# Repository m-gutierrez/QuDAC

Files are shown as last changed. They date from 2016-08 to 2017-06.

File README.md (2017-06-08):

# QuDAC

***TODO
+	Update performance measurements
+	include pin-out maps
+	link to ion trap theory, for voltage requirement definitions. 
+	include BOM
+	include assembly photos

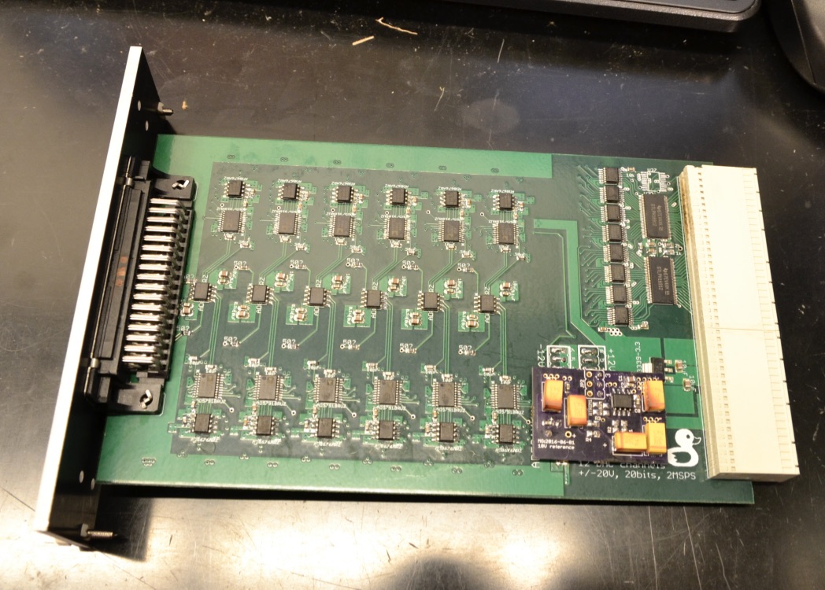
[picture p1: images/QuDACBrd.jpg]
QuDAC


This is a 12-channel 20-bit, +/-10V (+/-20V optional) 2MSPS DAC board designed for the Quanta rack system (QuACK). The card was designed to meet the system requirements described bellow while also being simple to populate and interface with the Quanta ion trap system vacuum chamber. Since we assemble these by-hand, we desired as few components as possible while still meeting the requirements of precision experiments with trapped ions. All components should be standard and easy to source, and if possible relatively cheap. A huge exception to the cheap criterion was the use of the ad5791 DAC chip, however there is a a slightly cheaper 18-bit ad5781 which is a drop-in replacement, and a significantly cheaper 16-bit version which requires modification for the different package size.

We've tested the cards at +/-10V, and have achieved reliable update rates at 2MSPS (above the 1.33MSPS datasheet spec for ad5791). Output slew's of ~50V/us have been measured on voltage swings >1V. Noise output is DAC-code dependent, currently limited by the reference-noise (~100nV/sqrt(Hz)). Which We've improved by using an adapter reference board with heavy filtering, 3-pole 1.5Hz cut-off RC filter with capacitors in a bootstrap configuration to minimize offset errors, which reduces the white-noise level to that dominated by the DAC and output op-amp of ~10-20nV/sqrt(Hz) white noise beyond 1kHz.

## Layout 

The board contains 6-layers. This was mostly due to a panel order with other designs requiring 6 layers. The board could easily be re-drawn with 4 layers.
The current layout is 

+	layer 1 - analog signals (top)
+	layer 2 - ground plane
+	layer 3 - analog signals
+	layer 4 - power planes
+	layer 5 - ground plane
+	layer 6 - digital signals (bot)

## component choice

The components where chosen to meet the system requirements, here is a list of the key QuDAC components with a list of the relevant performance spec's.

+	AD5791: DAC, 20-bit, +/-15V supply range, NSD <10nV/sqrt(Hz), 1-2MSPS update rate
+	AD8676: op-amp, +/-15V supply range, NSD <10nV/sqrt(Hz), 10MHz GBP
+	AD8620: op-amp, +/-12V supply range, NSD <10nV/sqrt(Hz), 50MHz GBP, <1us settling to 20-bit accuracy
+	See card-buffer for description of backplane interface.

## Application aim 

Trapped ion quantum computing (TIQC) requires dozens of independently controllable voltage sources with low noise (<100nV/sqrt(Hz)), wide-output range (+/-10V) and fast update rates (>1MSPS). These sources should be extend-able while maintaining synchronized updates, and allow for asynchronous clocking. 

### Output range

In the trap for our particular experiment, Sandia's high optical access trap (HOA v2), there are 96 independent control electrodes. With a trapping height ~68micron, an electrode pitch of ~70micron and control electrodes between the RF electrodes the HOA requires voltages of ~1-4V for trapping potentials producing secular frequencies $\omega_{sec} \approx 2\pi 1MHz$. And allows for +/-20V without damage to the on-chip RF-shunting capacitors. 

### Precision

### Noise level

For room temperature traps typical electric field noise at the ion, due to yet-unknown surface effects, is around ($S_{\nu} \approx 10 \mu V /m\sqrt{Hz}$), which corresponds to an electrode-voltage noise of (~100nV/sqrt(Hz)). Electric field noise in ion traps is a major concern for high fidelity operations, as current two-qubit gate mechanisms use the ions motional state and are first order sensitive to changes in the motional state during the gate operation. In order for gate fidelities to reach error correcting thresholds of ~1e-4 control-voltage noise must be kept well bellow this value. 

### Update rates

Control potentials used in TIQC is typically a compromise between many different concerns. One such concern is that the electric field noise spectrum typical goes as ~1/f such that increasing the secular frequencies is one way to reduce the error due to motional heating of the ion. Another is trap stability and overall trapping depth, since the axial-potential can easily over-take the radial psuedo-potential and reduce the trapping depth to zero. For the trapping dimensions typical used (heights of 50-150micron) useful compromises tend to be between 1-2MHz axial secular frequencies. 

This sets the time scale how changes to control voltages will affect the ions motion, i.e. the time scale for changes to be adiabatic or diabatic. We would like voltage updates to be on the order of or faster than the characteristic ion motion, so update rates exceeding 1MSPS and slew rates >1V/MHz are necessary to meet this constraint. 

### synchronized updates and clocking
The density of the DAC's per card and the clocking rate. where chosen to meet more general back-plane specifications, which takes into account additional devices of interest, clocking speeds, types of isolation achievable over various clock speeds and bus-size. In the end, a 36-bit backplane bus allows for 12-DAC's with independent sync,clock and data lines. In addition to these 36-bits there are an additional 8-bits which by-pass the card select buffers on the backplane interface, which we connect the DAC update pin (LDAC) to allowing multiple cards to be updated simultaneously. 

# Adapters 

There are 3 adapter cards used in our setup. Which assist in converting the card channels into the experiments two DB-50 connectors. 

## Combine2Cards
The first `Combine2Cards' allows us to combine two of the QuDAC cards into a single 24 channel output. The card can be placed directly on the cards within the rack, designed for accommodate the 7HP spacing of the QuACK system. The pin-out is made such that each control voltage is routed as a twisted pair with a ground wire using standard db50 cables. 

## 24CH-2x24CH
The second card, '24CH-2x24CH', copies one 24 channel output into 2 identical pin-out 24-channel outputs. Allowing 48 DAC's to control all 96 trap control voltages. The card also has a 3rd copy for probing voltage outputs.

## filterboard
The final card, 'filterboard', takes two 24-channel inputs and routes them into a single db50-connector. The board also contains 48 7-pole (or 3-pole) coilcraft.com LC filters. In our setup, these are 7-pole 300kHz LC-filters, providing 80db suppression at 1-2MHz. This board is intended to plug directly into the vacuum chamber experiment flange, which routes 100 control signals into the trap-chip through two DB-50 connectors. One of thees boards should also be configured with the resonator-line populated. On our setup, this line consists of a hand-wound ~500nH inductor, connecting to ~20pF trap capacitance producing a ~50MHz resonant frequency, and ~300pF of matching capacitance. The RF tap, consists of a high-voltage 0.2pF capacitor and a 100pF capacitor for a ~1/500 sampling voltage gain. 

# System performance

## range, offset and non-linearity

## noise spectral density

## update rate, slew rate, tone-purity

## synchronous update, clock noise

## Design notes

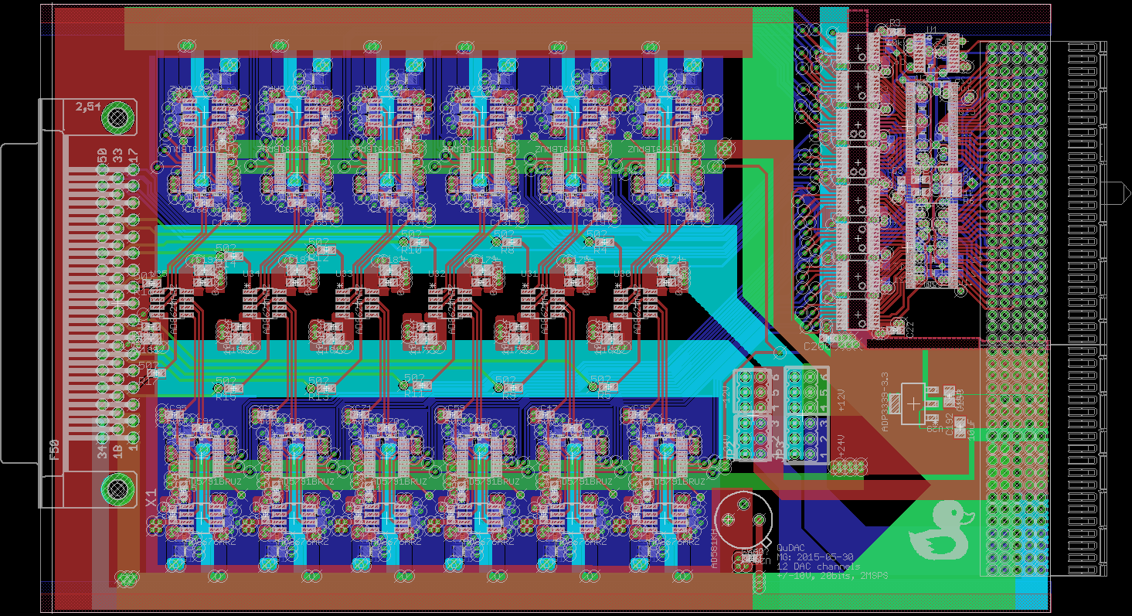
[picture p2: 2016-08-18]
images/QuDACBrd.png

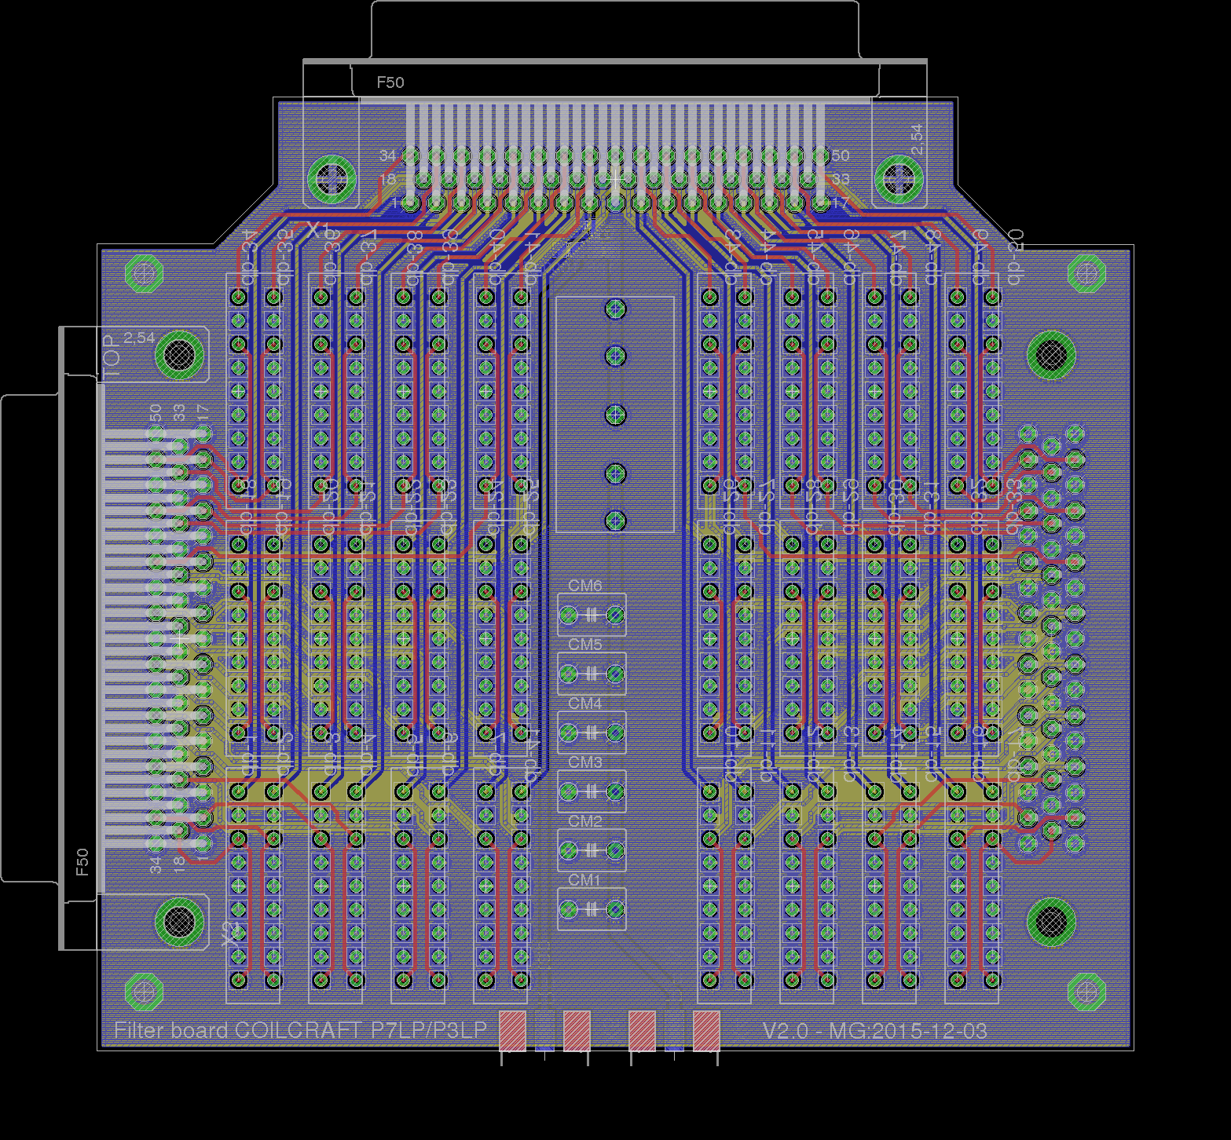
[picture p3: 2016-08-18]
images/filterboard.png

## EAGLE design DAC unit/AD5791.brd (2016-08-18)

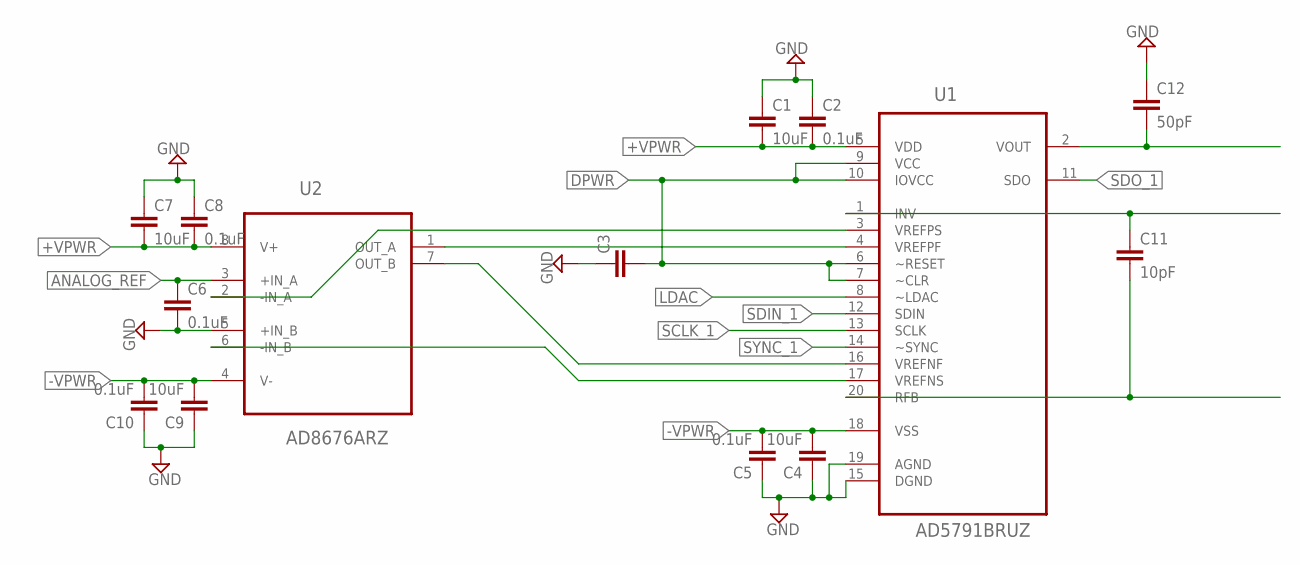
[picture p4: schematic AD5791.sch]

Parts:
C1, C4, C7, C9: 10uF; C0805
C2, C5, C6, C8, C10: 0.1uF; C0603
C3: CC0603; C0603
C11: 10pF; C0603
C12: 50pF; C0603
U1: AD5791BRUZ; SOP65P640X120-20N
U2: AD8676ARZ; SOIC127P600X175-8N

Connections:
+VPWR: C1.2, C2.2, C7.2, C8.2, U1.5 (VDD), U2.8 (V+)
-VPWR: C4.2, C5.2, C9.2, C10.2, U1.18 (VSS), U2.4 (V-)
ANALOG_REF: C6.1, U2.3 (+IN_A)
DPWR: C3.2, U1.6 (~RESET), U1.7 (~CLR), U1.9 (VCC), U1.10 (IOVCC)
GND: C1.1, C2.1, C3.1, C4.1, C5.1, C6.2, C7.1, C8.1, C9.1, C10.1, C12.1, U1.15 (DGND), U1.19 (AGND), U2.5 (+IN_B)
LDAC: U1.8 (~LDAC)
unnamed: U1.4 (VREFPF), U2.1 (OUT_A)
unnamed: U1.16 (VREFNF), U2.7 (OUT_B)
unnamed: U1.3 (VREFPS), U2.2 (-IN_A)
unnamed: U1.17 (VREFNS), U2.6 (-IN_B)
unnamed: C12.2, U1.2 (VOUT)
unnamed: C11.1, U1.1 (INV)
unnamed: C11.2, U1.20 (RFB)
SCLK_1: U1.13 (SCLK)
SDIN_1: U1.12 (SDIN)
SDO_1: U1.11 (SDO)
SYNC_1: U1.14 (~SYNC)

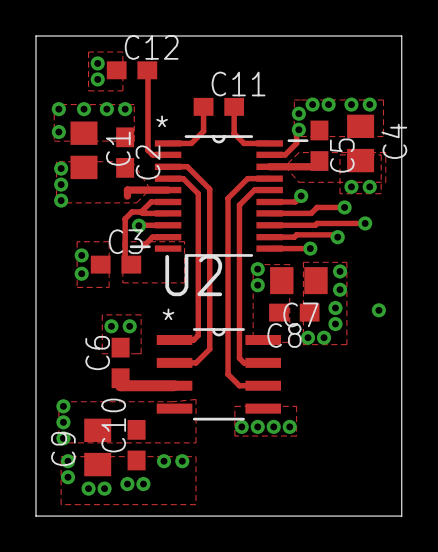
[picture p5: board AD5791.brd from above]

Board: 4 copper layers, 20.3 x 26.7 mm, 14 parts (0 on the bottom side), 12 nets.

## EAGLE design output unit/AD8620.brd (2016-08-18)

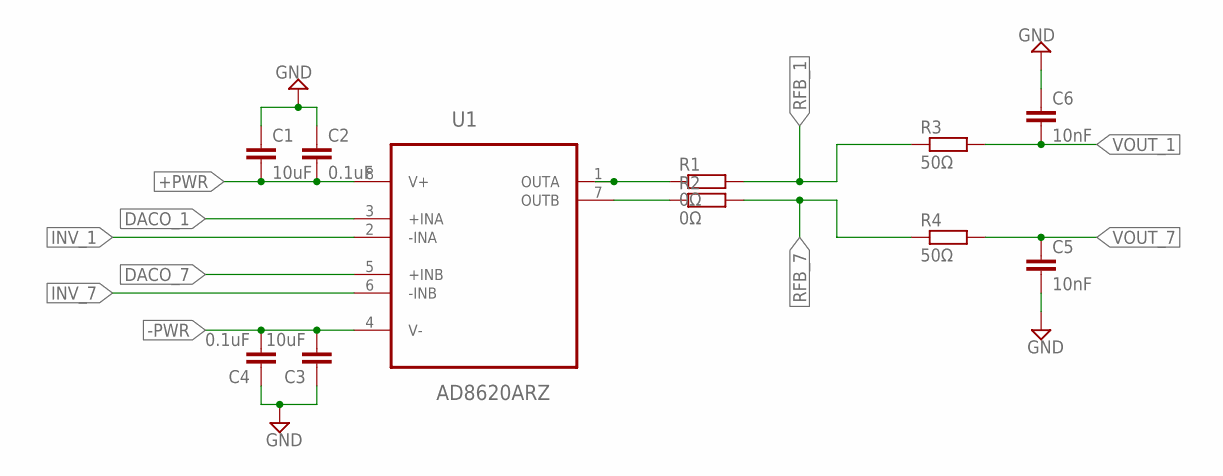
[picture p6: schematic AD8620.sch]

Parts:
C1, C3: 10uF; C0805
C2, C4: 0.1uF; C0603
C5, C6: 10nF; C0603
R1, R2: 0Ω; R0603
R3, R4: 50Ω; R0603
U1: AD8620ARZ; SOIC127P600X175-8N

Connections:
+PWR: C1.2, C2.2, U1.8 (V+)
-PWR: C3.2, C4.2, U1.4 (V-)
DACO_1: U1.3 (+INA)
DACO_7: U1.5 (+INB)
GND: C1.1, C2.1, C3.1, C4.1, C5.2, C6.1
INV_1: U1.2 (-INA)
INV_7: U1.6 (-INB)
unnamed: R1.1, U1.1 (OUTA)
unnamed: R2.1, U1.7 (OUTB)
RFB_1: R1.2, R3.1
RFB_7: R2.2, R4.1
VOUT_1: C6.2, R3.2
VOUT_7: C5.1, R4.2

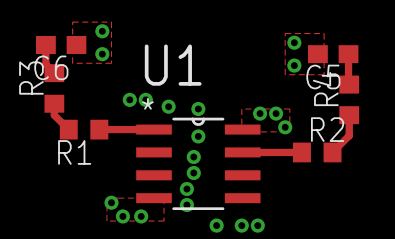
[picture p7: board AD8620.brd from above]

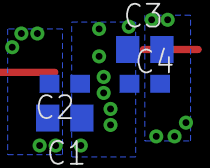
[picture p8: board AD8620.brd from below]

Board: 6 copper layers, 11 parts (4 on the bottom side), 9 nets.

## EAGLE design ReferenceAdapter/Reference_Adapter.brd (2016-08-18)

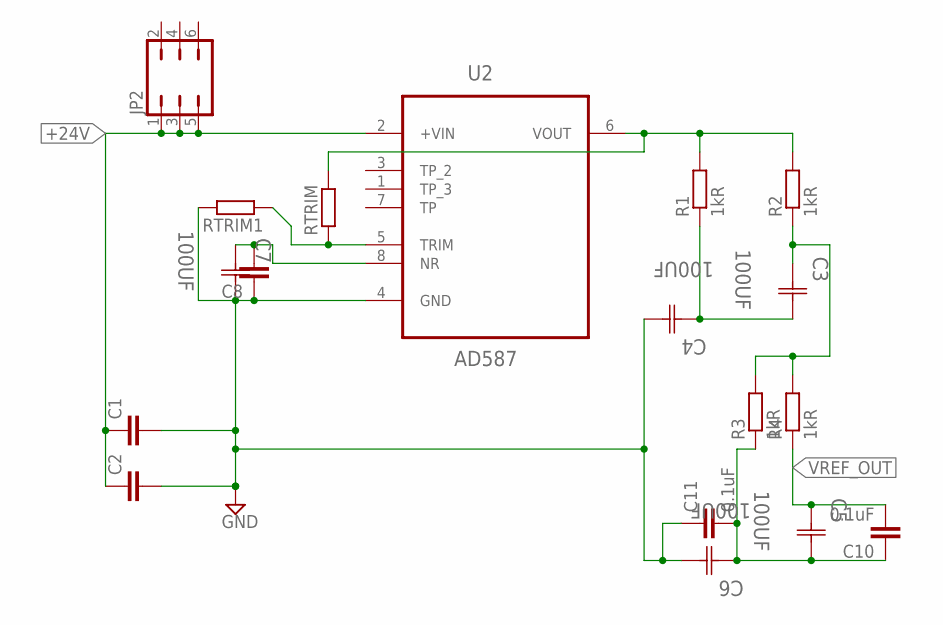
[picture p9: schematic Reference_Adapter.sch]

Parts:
C1, C8: C; C0805
C2: CC0603; C0603
C3, C4, C5, C6, C7: 100UF; CAPCP7343X430N
C10, C11: 0.1uF; C0603
JP2: JP3Q
R1, R2, R3, R4: 1kR; R0805
RTRIM, RTRIM1: R; R0805
U2: AD587; SOIC127P600X175-8N

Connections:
+24V: C1.1, C2.1, JP2.1, JP2.3, JP2.5, U2.2 (+VIN)
GND: C1.2, C2.2, C4.2, C6.2, C7.2, C8.1, C11.1, RTRIM1.2, U2.4 (GND)
unnamed: C3.2, C4.1, R1.1
unnamed: RTRIM.1, RTRIM1.1, U2.5 (TRIM)
unnamed: R1.2, R2.2, RTRIM.2, U2.6 (VOUT)
unnamed: C7.1, C8.2, U2.8 (NR)
unnamed: C3.1, R2.1, R3.2, R4.2
unnamed: C5.2, C6.1, C10.1, C11.2, R3.1
VREF_OUT: C5.1, C10.2, R4.1

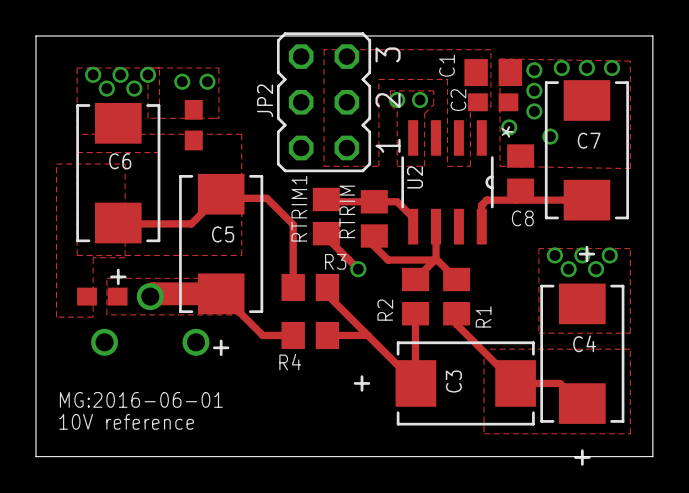
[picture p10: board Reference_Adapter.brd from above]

Board: 2 copper layers, 34.3 x 23.4 mm, 18 parts (0 on the bottom side), 9 nets.

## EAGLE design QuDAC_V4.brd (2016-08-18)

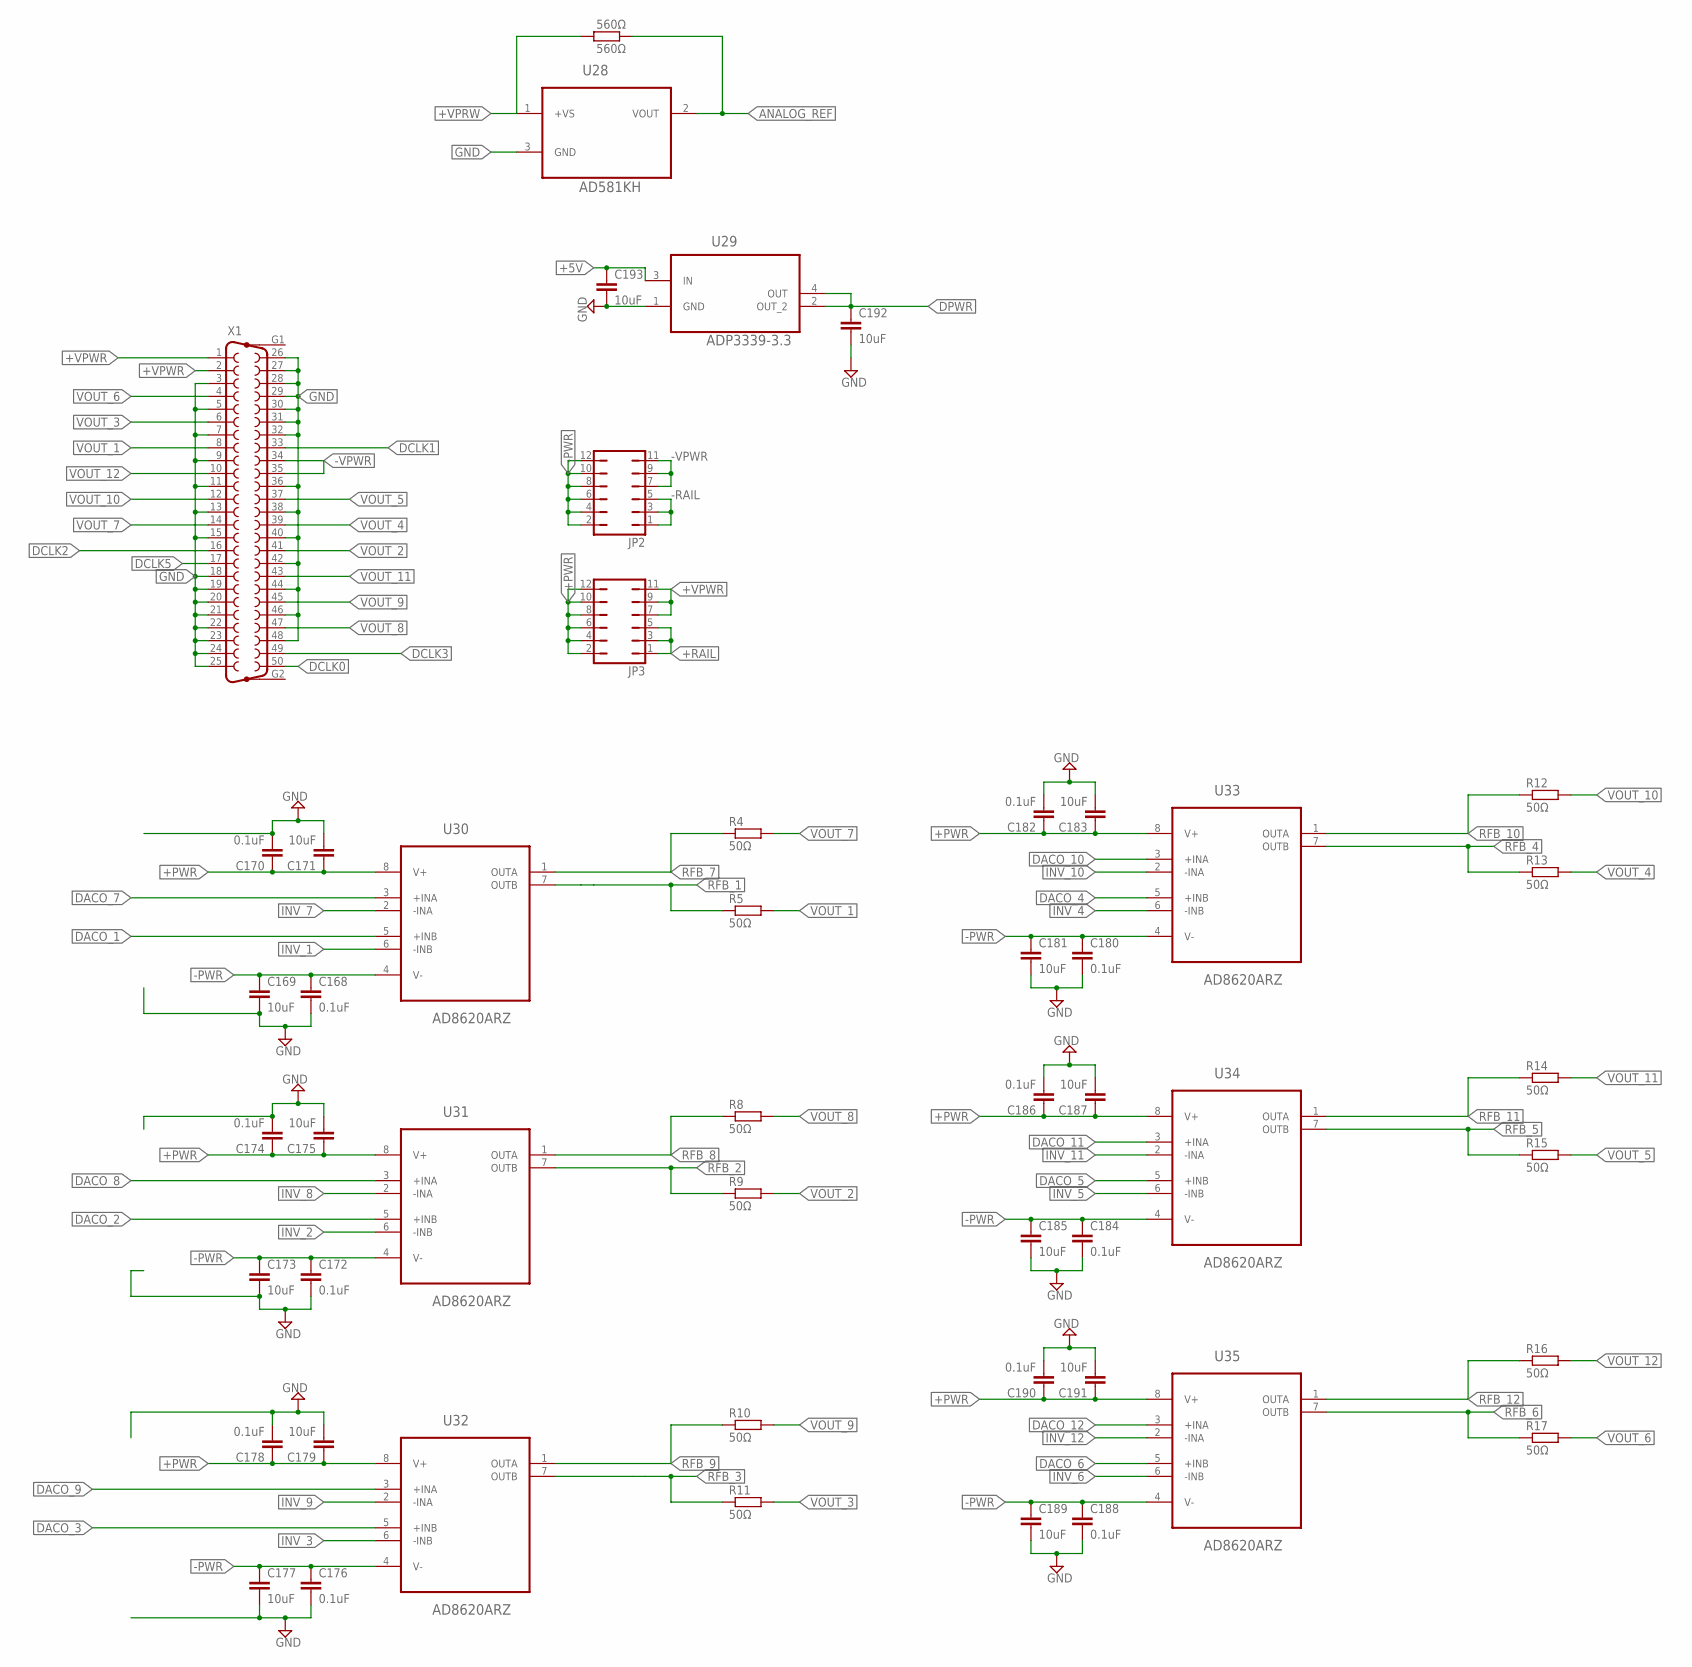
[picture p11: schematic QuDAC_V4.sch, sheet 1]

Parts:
560Ω: 560Ω; R0603
C168, C170, C172, C174, C176, C178, C180, C182, C184, C186, C188, C190: 0.1uF; C0603
C169, C171, C173, C175, C177, C179, C181, C183, C185, C187, C189, C191, C192, C193: 10uF; C0805
JP2, JP3: JP6Q
R4, R5, R8, R9, R10, R11, R12, R13, R14, R15, R16, R17: 50Ω; R0603
U28: AD581KH; TO254P939X470-3P
U29: ADP3339-3.3; SOT230P700X180-4N
U30, U31, U32, U33, U34, U35: AD8620ARZ; SOIC127P600X175-8N
X1: F50HP

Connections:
+5V: C193.1, U29.3 (IN); also elsewhere on the board
+PWR: C170.1, C171.1, C174.1, C175.1, C178.1, C179.1, C182.1, C183.1, C186.1, C187.1, C190.1, C191.1, JP3.2, JP3.4, JP3.6, JP3.8, JP3.10, JP3.12, U30.8 (V+), U31.8 (V+), U32.8 (V+), U33.8 (V+), U34.8 (V+), U35.8 (V+)
+RAIL: JP3.1, JP3.3, JP3.5; also elsewhere on the board
+VPRW: 560Ω.2, U28.1 (+VS)
+VPWR: JP3.7, JP3.9, JP3.11, X1.1, X1.2; also elsewhere on the board
-PWR: C168.1, C169.1, C172.1, C173.1, C176.1, C177.1, C180.1, C181.1, C184.1, C185.1, C188.1, C189.1, JP2.2, JP2.4, JP2.6, JP2.8, JP2.10, JP2.12, U30.4 (V-), U31.4 (V-), U32.4 (V-), U33.4 (V-), U34.4 (V-), U35.4 (V-)
-RAIL: JP2.1, JP2.3, JP2.5; also elsewhere on the board
-VPWR: JP2.7, JP2.9, JP2.11, X1.34, X1.35; also elsewhere on the board
ANALOG_REF: 560Ω.1, U28.2 (VOUT); also elsewhere on the board
DACO_1: U30.5 (+INB); also elsewhere on the board
DACO_2: U31.5 (+INB); also elsewhere on the board
DACO_3: U32.5 (+INB); also elsewhere on the board
DACO_4: U33.5 (+INB); also elsewhere on the board
DACO_5: U34.5 (+INB); also elsewhere on the board
DACO_6: U35.5 (+INB); also elsewhere on the board
DACO_7: U30.3 (+INA); also elsewhere on the board
DACO_8: U31.3 (+INA); also elsewhere on the board
DACO_9: U32.3 (+INA); also elsewhere on the board
DACO_10: U33.3 (+INA); also elsewhere on the board
DACO_11: U34.3 (+INA); also elsewhere on the board
DACO_12: U35.3 (+INA); also elsewhere on the board
DCLK0: X1.50; also elsewhere on the board
DCLK1: X1.33; also elsewhere on the board
DCLK2: X1.16; also elsewhere on the board
DCLK3: X1.49; also elsewhere on the board
DCLK5: X1.17; also elsewhere on the board
DPWR: C192.1, U29.2 (OUT_2), U29.4 (OUT); also elsewhere on the board
GND: C168.2, C169.2, C170.2, C171.2, C172.2, C173.2, C174.2, C175.2, C176.2, C177.2, C178.2, C179.2, C180.2, C181.2, C182.2, C183.2, C184.2, C185.2, C186.2, C187.2, C188.2, C189.2, C190.2, C191.2, C192.2, C193.2, U28.3 (GND), U29.1 (GND), X1.3, X1.5, X1.7, X1.9, X1.11, X1.13, X1.15, X1.18, X1.19, X1.20, X1.21, X1.22, X1.23, X1.24, X1.25, X1.26, X1.27, X1.28, X1.29, X1.30, X1.31, X1.32, X1.36, X1.38, X1.40, X1.42, X1.44, X1.46, X1.48; also elsewhere on the board
INV_1: U30.6 (-INB); also elsewhere on the board
INV_2: U31.6 (-INB); also elsewhere on the board
INV_3: U32.6 (-INB); also elsewhere on the board
INV_4: U33.6 (-INB); also elsewhere on the board
INV_5: U34.6 (-INB); also elsewhere on the board
INV_6: U35.6 (-INB); also elsewhere on the board
INV_7: U30.2 (-INA); also elsewhere on the board
INV_8: U31.2 (-INA); also elsewhere on the board
INV_9: U32.2 (-INA); also elsewhere on the board
INV_10: U33.2 (-INA); also elsewhere on the board
INV_11: U34.2 (-INA); also elsewhere on the board
INV_12: U35.2 (-INA); also elsewhere on the board
RFB_1: R5.1, U30.7 (OUTB); also elsewhere on the board
RFB_2: R9.1, U31.7 (OUTB); also elsewhere on the board
RFB_3: R11.1, U32.7 (OUTB); also elsewhere on the board
RFB_4: R13.1, U33.7 (OUTB); also elsewhere on the board
RFB_5: R15.1, U34.7 (OUTB); also elsewhere on the board
RFB_6: R17.1, U35.7 (OUTB); also elsewhere on the board
RFB_7: R4.1, U30.1 (OUTA); also elsewhere on the board
RFB_8: R8.1, U31.1 (OUTA); also elsewhere on the board
RFB_9: R10.1, U32.1 (OUTA); also elsewhere on the board
RFB_10: R12.1, U33.1 (OUTA); also elsewhere on the board
RFB_11: R14.1, U34.1 (OUTA); also elsewhere on the board
RFB_12: R16.1, U35.1 (OUTA); also elsewhere on the board
VOUT_1: R5.2, X1.8
VOUT_2: R9.2, X1.41
VOUT_3: R11.2, X1.6
VOUT_4: R13.2, X1.39
VOUT_5: R15.2, X1.37
VOUT_6: R17.2, X1.4
VOUT_7: R4.2, X1.14
VOUT_8: R8.2, X1.47
VOUT_9: R10.2, X1.45
VOUT_10: R12.2, X1.12
VOUT_11: R14.2, X1.43
VOUT_12: R16.2, X1.10

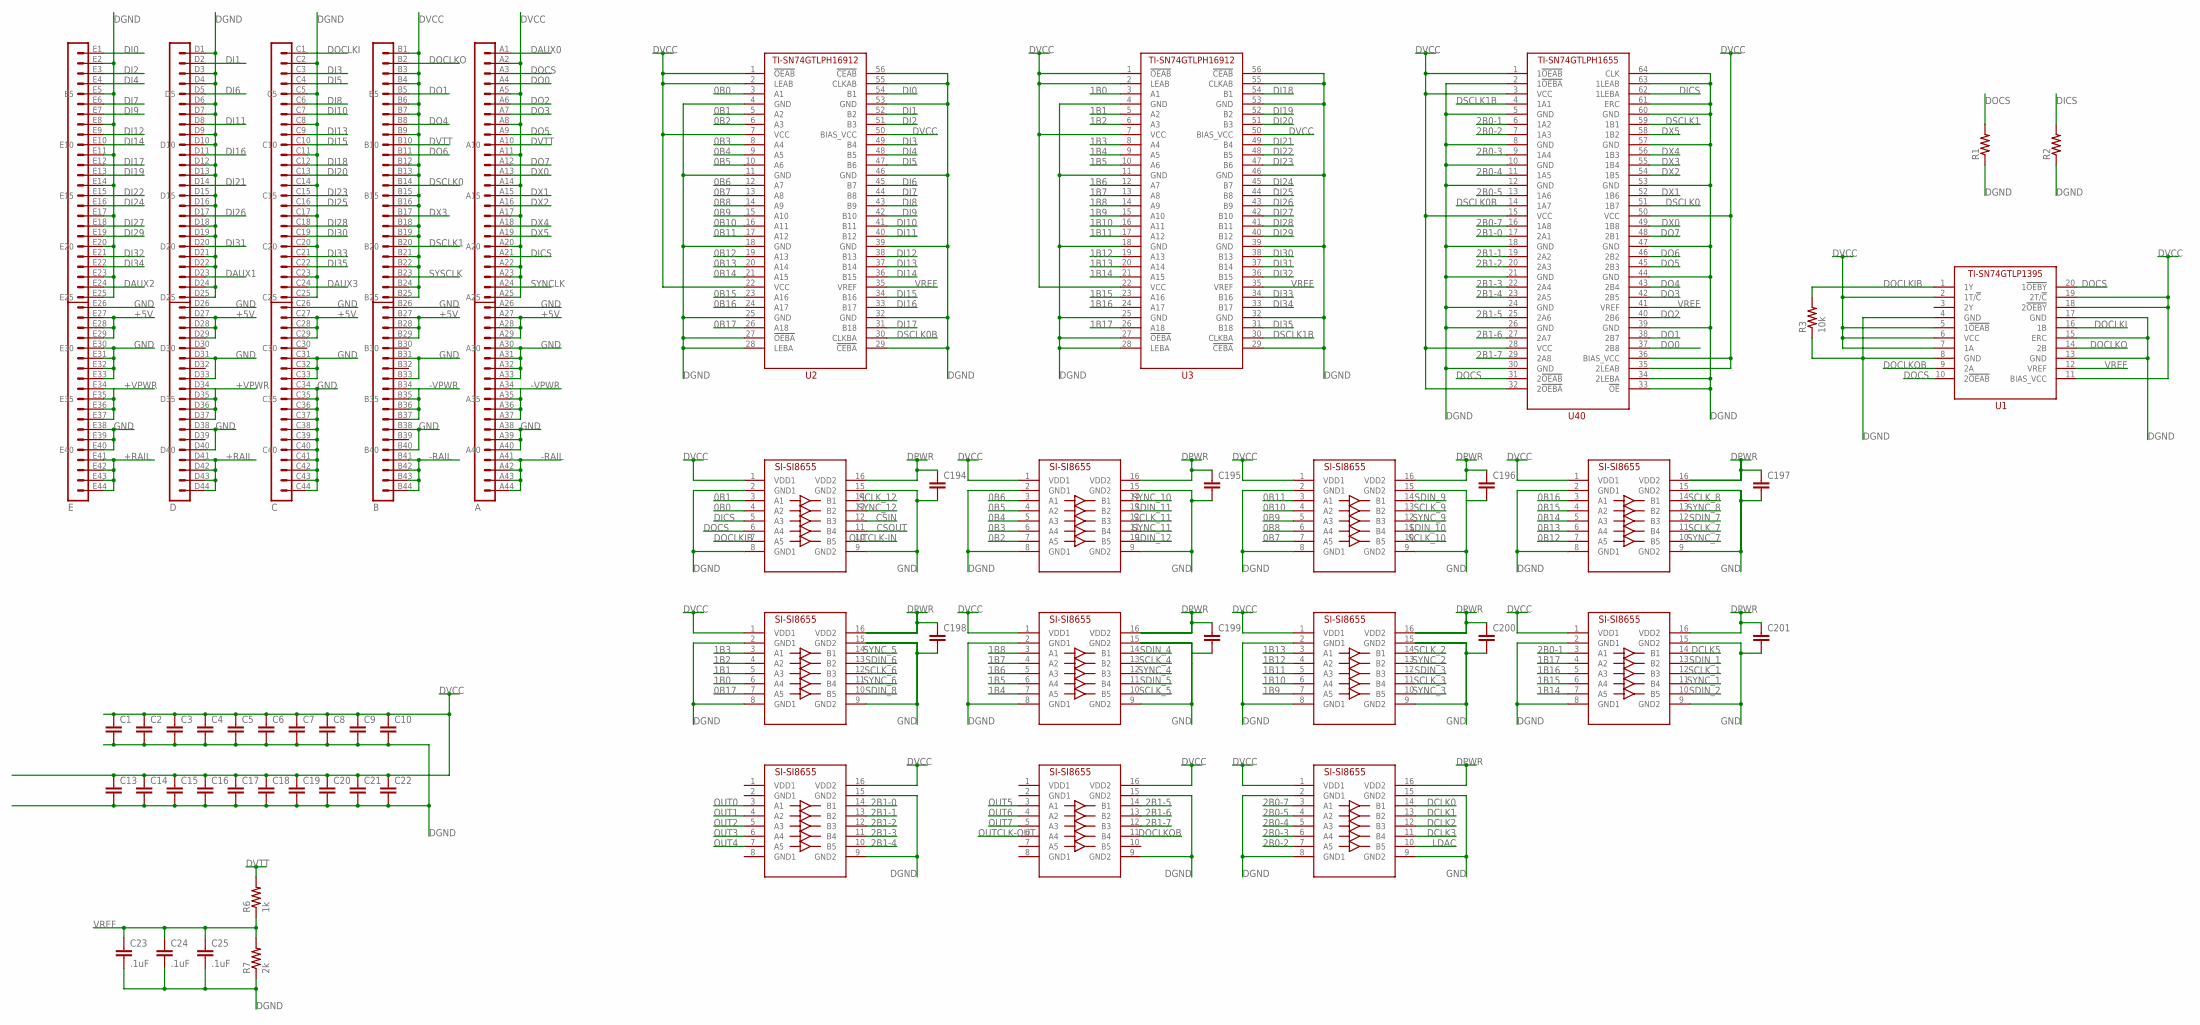
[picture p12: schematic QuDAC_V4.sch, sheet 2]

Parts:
C1, C2, C3, C4, C5, C6, C7, C8, C9, C10, C13, C14, C15, C16, C17, C18, C19, C20, C21, C22, C194, C195, C196, C197, C198, C199, C200, C201: CC0603; C0603
C23, C24, C25: .1uF; C0603
ISO1, ISO2, ISO3, ISO4, ISO5, ISO6, ISO7, ISO8, ISO9, ISO10, ISO11: SI-SI8655; QSOP-16
J1: EUROCARD-CPCI-220EUROCARD-B19+AB25-NOFRONTDIM; EUROCARD-CPCI-B19+1B25-NOFRONTDIM
R1, R2: R-US_R0603; R0603
R3: 10k; R0603
R6: 1k; R0805
R7: 2k; R0805
U1: TI-SN74GTLP1395; TSSOP-20
U2, U3: TI-SN74GTLPH16912; TSSOP-56
U40: TI-SN74GTLPH1655; TSSOP-64

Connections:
0B0: ISO1.4 (A2), U2.3 (A1)
0B1: ISO1.3 (A1), U2.5 (A2)
0B2: ISO2.7 (A5), U2.6 (A3)
0B3: ISO2.6 (A4), U2.8 (A4)
0B4: ISO2.5 (A3), U2.9 (A5)
0B5: ISO2.4 (A2), U2.10 (A6)
0B6: ISO2.3 (A1), U2.12 (A7)
0B7: ISO3.7 (A5), U2.13 (A8)
0B8: ISO3.6 (A4), U2.14 (A9)
0B9: ISO3.5 (A3), U2.15 (A10)
0B10: ISO3.4 (A2), U2.16 (A11)
0B11: ISO3.3 (A1), U2.17 (A12)
0B12: ISO4.7 (A5), U2.19 (A13)
0B13: ISO4.6 (A4), U2.20 (A14)
0B14: ISO4.5 (A3), U2.21 (A15)
0B15: ISO4.4 (A2), U2.23 (A16)
0B16: ISO4.3 (A1), U2.24 (A17)
0B17: ISO5.7 (A5), U2.26 (A18)
1B0: ISO5.6 (A4), U3.3 (A1)
1B1: ISO5.5 (A3), U3.5 (A2)
1B2: ISO5.4 (A2), U3.6 (A3)
1B3: ISO5.3 (A1), U3.8 (A4)
1B4: ISO6.7 (A5), U3.9 (A5)
1B5: ISO6.6 (A4), U3.10 (A6)
1B6: ISO6.5 (A3), U3.12 (A7)
1B7: ISO6.4 (A2), U3.13 (A8)
1B8: ISO6.3 (A1), U3.14 (A9)
1B9: ISO7.7 (A5), U3.15 (A10)
1B10: ISO7.6 (A4), U3.16 (A11)
1B11: ISO7.5 (A3), U3.17 (A12)
1B12: ISO7.4 (A2), U3.19 (A13)
1B13: ISO7.3 (A1), U3.20 (A14)
1B14: ISO8.7 (A5), U3.21 (A15)
1B15: ISO8.6 (A4), U3.23 (A16)
1B16: ISO8.5 (A3), U3.24 (A17)
1B17: ISO8.4 (A2), U3.26 (A18)
2B0-1: ISO8.3 (A1), U40.6 (1A2)
2B0-2: ISO11.7 (A5), U40.7 (1A3)
2B0-3: ISO11.6 (A4), U40.9 (1A4)
2B0-4: ISO11.5 (A3), U40.11 (1A5)
2B0-5: ISO11.4 (A2), U40.13 (1A6)
2B0-7: ISO11.3 (A1), U40.16 (1A8)
2B1-0: ISO9.14 (B1), U40.17 (2A1)
2B1-1: ISO9.13 (B2), U40.19 (2A2)
2B1-2: ISO9.12 (B3), U40.20 (2A3)
2B1-3: ISO9.11 (B4), U40.22 (2A4)
2B1-4: ISO9.10 (B5), U40.23 (2A5)
2B1-5: ISO10.14 (B1), U40.25 (2A6)
2B1-6: ISO10.13 (B2), U40.27 (2A7)
2B1-7: ISO10.12 (B3), U40.29 (2A8)
+5V: J1.A27, J1.A28, J1.A29, J1.B27, J1.B28, J1.B29, J1.C27, J1.C28, J1.C29, J1.D27, J1.D28, J1.D29, J1.E27, J1.E28, J1.E29; also elsewhere on the board
+RAIL: J1.D41, J1.D42, J1.D43, J1.D44, J1.E41, J1.E42, J1.E43, J1.E44; also elsewhere on the board
+VPWR: J1.D34, J1.D35, J1.D36, J1.D37, J1.E34, J1.E35, J1.E36, J1.E37; also elsewhere on the board
-RAIL: J1.A41, J1.A42, J1.A43, J1.A44, J1.B41, J1.B42, J1.B43, J1.B44; also elsewhere on the board
-VPWR: J1.A34, J1.A35, J1.A36, J1.A37, J1.B34, J1.B35, J1.B36, J1.B37; also elsewhere on the board
CSIN: ISO1.12 (B3)
CSOUT: ISO1.11 (B4)
DAUX0: J1.A1
DAUX1: J1.D23
DAUX2: J1.E24
DAUX3: J1.C24
DCLK0: ISO11.14 (B1); also elsewhere on the board
DCLK1: ISO11.13 (B2); also elsewhere on the board
DCLK2: ISO11.12 (B3); also elsewhere on the board
DCLK3: ISO11.11 (B4); also elsewhere on the board
DCLK5: ISO8.14 (B1); also elsewhere on the board
DGND: C1.2, C2.2, C3.2, C4.2, C5.2, C6.2, C7.2, C8.2, C9.2, C10.2, C13.2, C14.2, C15.2, C16.2, C17.2, C18.2, C19.2, C20.2, C21.2, C22.2, C23.2, C24.2, C25.2, ISO1.2 (GND1), ISO1.8 (GND1), ISO2.2 (GND1), ISO2.8 (GND1), ISO3.2 (GND1), ISO3.8 (GND1), ISO4.2 (GND1), ISO4.8 (GND1), ISO5.2 (GND1), ISO5.8 (GND1), ISO6.2 (GND1), ISO6.8 (GND1), ISO7.2 (GND1), ISO7.8 (GND1), ISO8.2 (GND1), ISO8.8 (GND1), ISO9.9 (GND2), ISO9.15 (GND2), ISO10.9 (GND2), ISO10.15 (GND2), ISO11.2 (GND1), ISO11.8 (GND1), J1.C2, J1.C5, J1.C8, J1.C11, J1.C14, J1.C17, J1.C20, J1.C23, J1.C25, J1.D1, J1.D3, J1.D4, J1.D6, J1.D7, J1.D9, J1.D10, J1.D12, J1.D13, J1.D15, J1.D16, J1.D18, J1.D19, J1.D21, J1.D22, J1.D24, J1.D25, J1.E2, J1.E5, J1.E8, J1.E11, J1.E14, J1.E17, J1.E20, J1.E23, J1.E25, R1.1, R2.1, R3.1, R7.1, U1.4 (GND), U1.8 (GND), U1.13 (GND), U1.15 (ERC), U1.17 (GND), U2.4 (GND), U2.11 (GND), U2.18 (GND), U2.25 (GND), U2.27 (!OEBA), U2.28 (LEBA), U2.29 (!CEBA), U2.32 (GND), U2.39 (GND), U2.46 (GND), U2.53 (GND), U2.55 (CLKAB), U2.56 (!CEAB), U3.4 (GND), U3.11 (GND), U3.18 (GND), U3.25 (GND), U3.27 (!OEBA), U3.28 (LEBA), U3.29 (!CEBA), U3.32 (GND), U3.39 (GND), U3.46 (GND), U3.53 (GND), U3.55 (CLKAB), U3.56 (!CEAB), U40.2 (1!OEBA), U40.5 (GND), U40.8 (GND), U40.10 (GND), U40.12 (GND), U40.18 (GND), U40.21 (GND), U40.24 (GND), U40.26 (GND), U40.30 (GND), U40.33 (!OE), U40.34 (2LEBA), U40.39 (GND), U40.44 (GND), U40.47 (GND), U40.53 (GND), U40.57 (GND), U40.60 (GND), U40.61 (ERC), U40.63 (1LEAB), U40.64 (CLK)
DI0: J1.E1, U2.54 (B1)
DI1: J1.D2, U2.52 (B2)
DI2: J1.E3, U2.51 (B3)
DI3: J1.C3, U2.49 (B4)
DI4: J1.E4, U2.48 (B5)
DI5: J1.C4, U2.47 (B6)
DI6: J1.D5, U2.45 (B7)
DI7: J1.E6, U2.44 (B8)
DI8: J1.C6, U2.43 (B9)
DI9: J1.E7, U2.42 (B10)
DI10: J1.C7, U2.41 (B11)
DI11: J1.D8, U2.40 (B12)
DI12: J1.E9, U2.38 (B13)
DI13: J1.C9, U2.37 (B14)
DI14: J1.E10, U2.36 (B15)
DI15: J1.C10, U2.34 (B16)
DI16: J1.D11, U2.33 (B17)
DI17: J1.E12, U2.31 (B18)
DI18: J1.C12, U3.54 (B1)
DI19: J1.E13, U3.52 (B2)
DI20: J1.C13, U3.51 (B3)
DI21: J1.D14, U3.49 (B4)
DI22: J1.E15, U3.48 (B5)
DI23: J1.C15, U3.47 (B6)
DI24: J1.E16, U3.45 (B7)
DI25: J1.C16, U3.44 (B8)
DI26: J1.D17, U3.43 (B9)
DI27: J1.E18, U3.42 (B10)
DI28: J1.C18, U3.41 (B11)
DI29: J1.E19, U3.40 (B12)
DI30: J1.C19, U3.38 (B13)
DI31: J1.D20, U3.37 (B14)
DI32: J1.E21, U3.36 (B15)
DI33: J1.C21, U3.34 (B16)
DI34: J1.E22, U3.33 (B17)
DI35: J1.C22, U3.31 (B18)
DICS: ISO1.5 (A3), J1.A21, R2.2, U40.62 (1LEBA)
DO0: J1.A4, U40.37 (2B8)
DO1: J1.B5, U40.38 (2B7)
DO2: J1.A6, U40.40 (2B6)
DO3: J1.A7, U40.42 (2B5)
DO4: J1.B8, U40.43 (2B4)
DO5: J1.A9, U40.45 (2B3)
DO6: J1.B11, U40.46 (2B2)
DO7: J1.A12, U40.48 (2B1)
DOCLKI: J1.C1, U1.16 (1B)
DOCLKIB: ISO1.7 (A5), R3.2, U1.1 (1Y)
DOCLKO: J1.B2, U1.14 (2B)
DOCLKOB: ISO10.11 (B4), U1.9 (2A)
DOCS: ISO1.6 (A4), J1.A3, R1.2, U1.10 (2!OEAB), U1.20 (1!OEBY), U40.31 (2!OEAB)
DPWR: C194.1, C195.1, C196.1, C197.1, C198.1, C199.1, C200.1, C201.1, ISO1.16 (VDD2), ISO2.16 (VDD2), ISO3.16 (VDD2), ISO4.16 (VDD2), ISO5.16 (VDD2), ISO6.16 (VDD2), ISO7.16 (VDD2), ISO8.16 (VDD2), ISO11.16 (VDD2); also elsewhere on the board
DSCLK0: J1.B14, U40.51 (1B7)
DSCLK0B: U2.30 (CLKBA), U40.14 (1A7)
DSCLK1: J1.B20, U40.59 (1B1)
DSCLK1B: U3.30 (CLKBA), U40.4 (1A1)
DVCC: C1.1, C2.1, C3.1, C4.1, C5.1, C6.1, C7.1, C8.1, C9.1, C10.1, C13.1, C14.1, C15.1, C16.1, C17.1, C18.1, C19.1, C20.1, C21.1, C22.1, ISO1.1 (VDD1), ISO2.1 (VDD1), ISO3.1 (VDD1), ISO4.1 (VDD1), ISO5.1 (VDD1), ISO6.1 (VDD1), ISO7.1 (VDD1), ISO8.1 (VDD1), ISO9.16 (VDD2), ISO10.16 (VDD2), ISO11.1 (VDD1), J1.A2, J1.A5, J1.A8, J1.A11, J1.A14, J1.A17, J1.A20, J1.A22, J1.A23, J1.A25, J1.B1, J1.B3, J1.B4, J1.B6, J1.B7, J1.B9, J1.B12, J1.B13, J1.B15, J1.B16, J1.B18, J1.B19, J1.B21, J1.B22, J1.B24, J1.B25, U1.2 (1T/!C), U1.5 (1!OEAB), U1.6 (VCC), U1.7 (1A), U1.11 (BIAS_VCC), U1.18 (2!OEBY), U1.19 (2T/!C), U2.1 (!OEAB), U2.2 (LEAB), U2.7 (VCC), U2.22 (VCC), U2.50 (BIAS_VCC), U3.1 (!OEAB), U3.2 (LEAB), U3.7 (VCC), U3.22 (VCC), U3.50 (BIAS_VCC), U40.1 (1!OEAB), U40.3 (VCC), U40.15 (VCC), U40.28 (VCC), U40.32 (2!OEBA), U40.35 (2LEAB), U40.36 (BIAS_VCC), U40.50 (VCC)
DVTT: J1.A10, J1.B10, R6.2
DX0: J1.A13, U40.49 (1B8)
DX1: J1.A15, U40.52 (1B6)
DX2: J1.A16, U40.54 (1B5)
DX3: J1.B17, U40.55 (1B4)
DX4: J1.A18, U40.56 (1B3)
DX5: J1.A19, U40.58 (1B2)
GND: C194.2, C195.2, C196.2, C197.2, C198.2, C199.2, C200.2, C201.2, ISO1.9 (GND2), ISO1.15 (GND2), ISO2.9 (GND2), ISO2.15 (GND2), ISO3.9 (GND2), ISO3.15 (GND2), ISO4.9 (GND2), ISO4.15 (GND2), ISO5.9 (GND2), ISO5.15 (GND2), ISO6.9 (GND2), ISO6.15 (GND2), ISO7.9 (GND2), ISO7.15 (GND2), ISO8.9 (GND2), ISO8.15 (GND2), ISO11.9 (GND2), ISO11.15 (GND2), J1.A26, J1.A30, J1.A31, J1.A32, J1.A33, J1.A38, J1.A39, J1.A40, J1.B26, J1.B31, J1.B33, J1.B38, J1.B40, J1.C26, J1.C31, J1.C32, J1.C33, J1.C34, J1.C35, J1.C36, J1.C37, J1.C38, J1.C39, J1.C40, J1.C41, J1.C42, J1.C43, J1.C44, J1.D26, J1.D31, J1.D33, J1.D38, J1.D40, J1.E26, J1.E30, J1.E31, J1.E32, J1.E33, J1.E38, J1.E39, J1.E40; also elsewhere on the board
LDAC: ISO11.10 (B5); also elsewhere on the board
OUT0: ISO9.3 (A1)
OUT1: ISO9.4 (A2)
OUT2: ISO9.5 (A3)
OUT3: ISO9.6 (A4)
OUT4: ISO9.7 (A5)
OUT5: ISO10.3 (A1)
OUT6: ISO10.4 (A2)
OUT7: ISO10.5 (A3)
OUTCLK-IN: ISO1.10 (B5)
OUTCLK-OUT: ISO10.6 (A4)
SCLK_1: ISO8.12 (B3); also elsewhere on the board
SCLK_2: ISO7.14 (B1); also elsewhere on the board
SCLK_3: ISO7.11 (B4); also elsewhere on the board
SCLK_4: ISO6.13 (B2); also elsewhere on the board
SCLK_5: ISO6.10 (B5); also elsewhere on the board
SCLK_6: ISO5.12 (B3); also elsewhere on the board
SCLK_7: ISO4.11 (B4); also elsewhere on the board
SCLK_8: ISO4.14 (B1); also elsewhere on the board
SCLK_9: ISO3.13 (B2); also elsewhere on the board
SCLK_10: ISO3.10 (B5); also elsewhere on the board
SCLK_11: ISO2.12 (B3); also elsewhere on the board
SCLK_12: ISO1.14 (B1); also elsewhere on the board
SDIN_1: ISO8.13 (B2); also elsewhere on the board
SDIN_2: ISO8.10 (B5); also elsewhere on the board
SDIN_3: ISO7.12 (B3); also elsewhere on the board
SDIN_4: ISO6.14 (B1); also elsewhere on the board
SDIN_5: ISO6.11 (B4); also elsewhere on the board
SDIN_6: ISO5.13 (B2); also elsewhere on the board
SDIN_7: ISO4.12 (B3); also elsewhere on the board
SDIN_8: ISO5.10 (B5); also elsewhere on the board
SDIN_9: ISO3.14 (B1); also elsewhere on the board
SDIN_10: ISO3.11 (B4); also elsewhere on the board
SDIN_11: ISO2.13 (B2); also elsewhere on the board
SDIN_12: ISO2.10 (B5); also elsewhere on the board
SYNCLK: J1.A24
SYNC_1: ISO8.11 (B4); also elsewhere on the board
SYNC_2: ISO7.13 (B2); also elsewhere on the board
SYNC_3: ISO7.10 (B5); also elsewhere on the board
SYNC_4: ISO6.12 (B3); also elsewhere on the board
SYNC_5: ISO5.14 (B1); also elsewhere on the board
SYNC_6: ISO5.11 (B4); also elsewhere on the board
SYNC_7: ISO4.10 (B5); also elsewhere on the board
SYNC_8: ISO4.13 (B2); also elsewhere on the board
SYNC_9: ISO3.12 (B3); also elsewhere on the board
SYNC_10: ISO2.14 (B1); also elsewhere on the board
SYNC_11: ISO2.11 (B4); also elsewhere on the board
SYNC_12: ISO1.13 (B2); also elsewhere on the board
SYSCLK: J1.B23
VREF: C23.1, C24.1, C25.1, R6.1, R7.2, U1.12 (VREF), U2.35 (VREF), U3.35 (VREF), U40.41 (VREF)

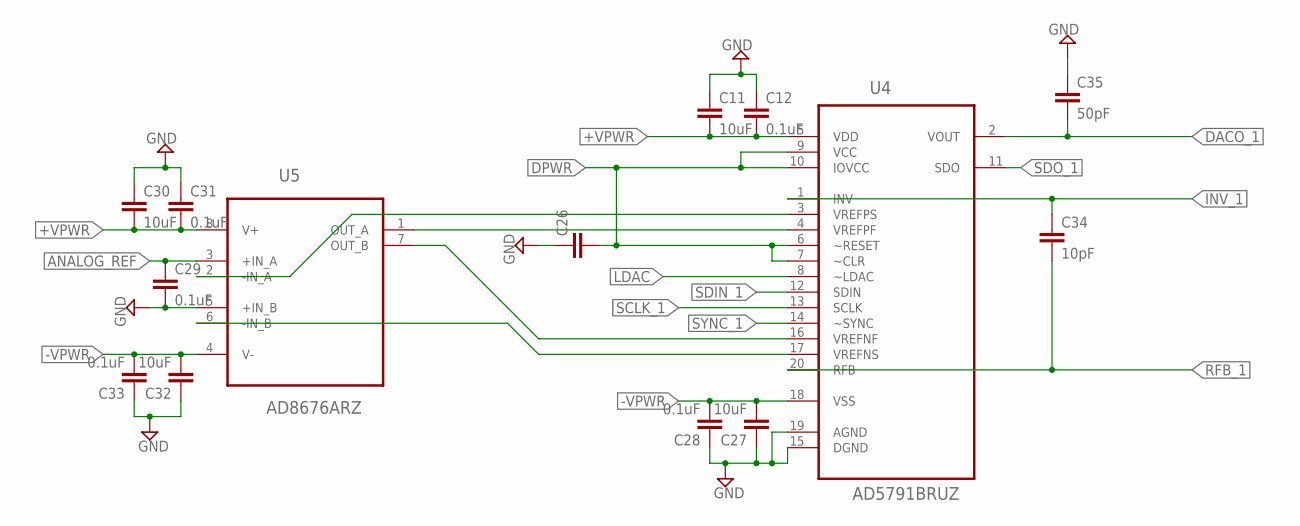
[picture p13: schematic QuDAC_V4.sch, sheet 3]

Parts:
C11, C27, C30, C32: 10uF; C0805
C12, C28, C29, C31, C33: 0.1uF; C0603
C26: CC0603; C0603
C34: 10pF; C0603
C35: 50pF; C0603
U4: AD5791BRUZ; SOP65P640X120-20N
U5: AD8676ARZ; SOIC127P600X175-8N

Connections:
+VPWR: C11.2, C12.2, C30.2, C31.2, U4.5 (VDD), U5.8 (V+); also elsewhere on the board
-VPWR: C27.2, C28.2, C32.2, C33.2, U4.18 (VSS), U5.4 (V-); also elsewhere on the board
ANALOG_REF: C29.1, U5.3 (+IN_A); also elsewhere on the board
DACO_1: C35.2, U4.2 (VOUT); also elsewhere on the board
DPWR: C26.2, U4.6 (~RESET), U4.7 (~CLR), U4.9 (VCC), U4.10 (IOVCC); also elsewhere on the board
GND: C11.1, C12.1, C26.1, C27.1, C28.1, C29.2, C30.1, C31.1, C32.1, C33.1, C35.1, U4.15 (DGND), U4.19 (AGND), U5.5 (+IN_B); also elsewhere on the board
INV_1: C34.1, U4.1 (INV); also elsewhere on the board
LDAC: U4.8 (~LDAC); also elsewhere on the board
unnamed: U4.4 (VREFPF), U5.1 (OUT_A)
unnamed: U4.16 (VREFNF), U5.7 (OUT_B)
unnamed: U4.3 (VREFPS), U5.2 (-IN_A)
unnamed: U4.17 (VREFNS), U5.6 (-IN_B)
RFB_1: C34.2, U4.20 (RFB); also elsewhere on the board
SCLK_1: U4.13 (SCLK); also elsewhere on the board
SDIN_1: U4.12 (SDIN); also elsewhere on the board
SDO_1: U4.11 (SDO)
SYNC_1: U4.14 (~SYNC); also elsewhere on the board

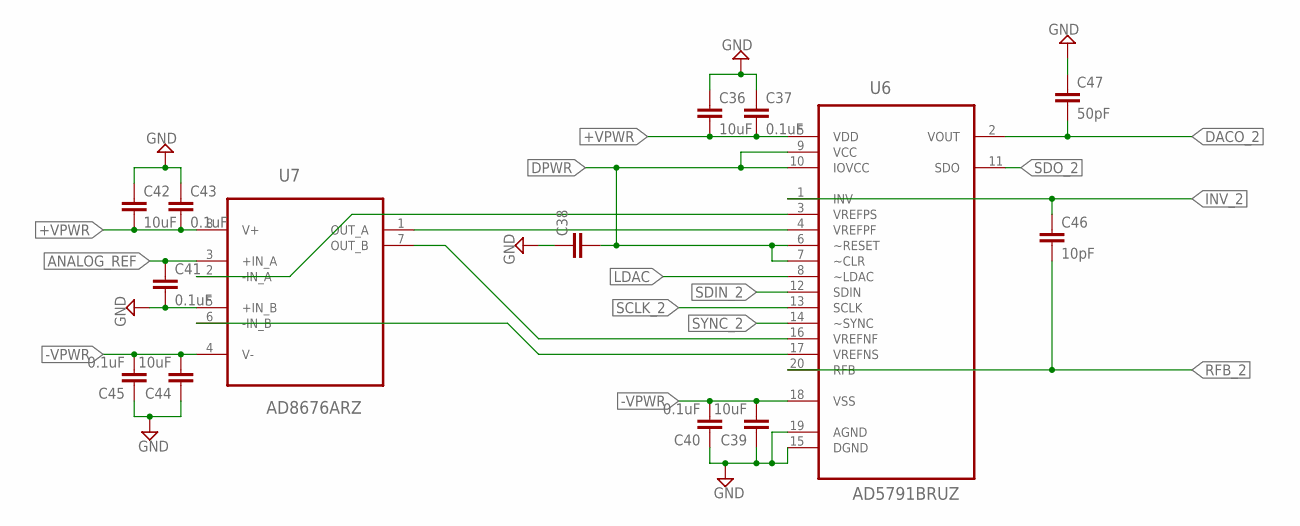
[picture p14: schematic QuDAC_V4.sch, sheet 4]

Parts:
C36, C39, C42, C44: 10uF; C0805
C37, C40, C41, C43, C45: 0.1uF; C0603
C38: CC0603; C0603
C46: 10pF; C0603
C47: 50pF; C0603
U6: AD5791BRUZ; SOP65P640X120-20N
U7: AD8676ARZ; SOIC127P600X175-8N

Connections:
+VPWR: C36.2, C37.2, C42.2, C43.2, U6.5 (VDD), U7.8 (V+); also elsewhere on the board
-VPWR: C39.2, C40.2, C44.2, C45.2, U6.18 (VSS), U7.4 (V-); also elsewhere on the board
ANALOG_REF: C41.1, U7.3 (+IN_A); also elsewhere on the board
DACO_2: C47.2, U6.2 (VOUT); also elsewhere on the board
DPWR: C38.2, U6.6 (~RESET), U6.7 (~CLR), U6.9 (VCC), U6.10 (IOVCC); also elsewhere on the board
GND: C36.1, C37.1, C38.1, C39.1, C40.1, C41.2, C42.1, C43.1, C44.1, C45.1, C47.1, U6.15 (DGND), U6.19 (AGND), U7.5 (+IN_B); also elsewhere on the board
INV_2: C46.1, U6.1 (INV); also elsewhere on the board
LDAC: U6.8 (~LDAC); also elsewhere on the board
unnamed: U6.4 (VREFPF), U7.1 (OUT_A)
unnamed: U6.16 (VREFNF), U7.7 (OUT_B)
unnamed: U6.3 (VREFPS), U7.2 (-IN_A)
unnamed: U6.17 (VREFNS), U7.6 (-IN_B)
RFB_2: C46.2, U6.20 (RFB); also elsewhere on the board
SCLK_2: U6.13 (SCLK); also elsewhere on the board
SDIN_2: U6.12 (SDIN); also elsewhere on the board
SDO_2: U6.11 (SDO)
SYNC_2: U6.14 (~SYNC); also elsewhere on the board

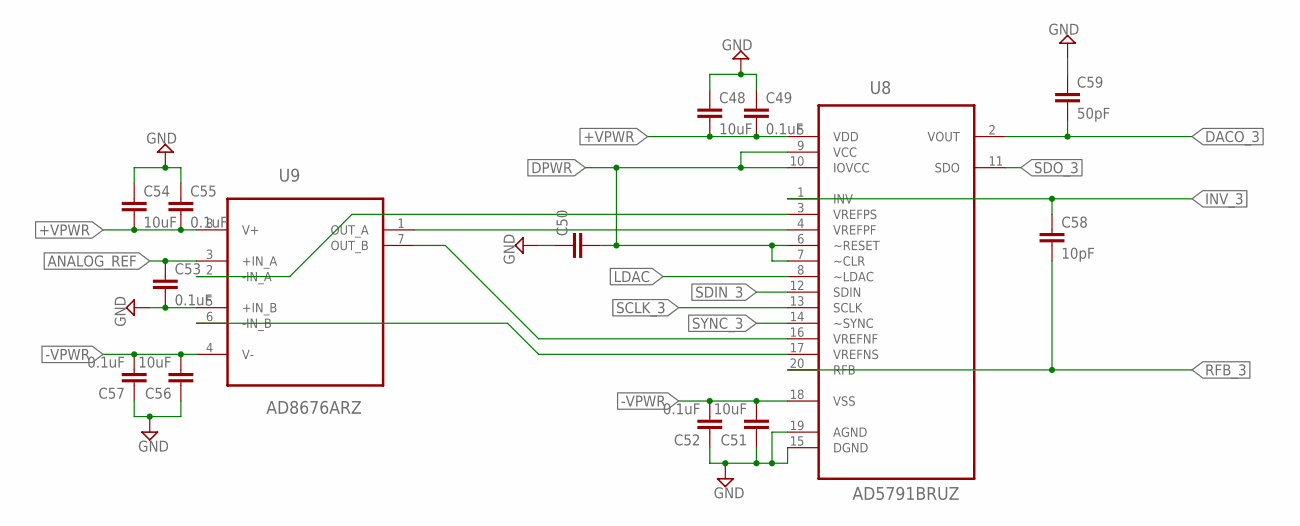
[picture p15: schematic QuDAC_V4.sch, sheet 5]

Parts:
C48, C51, C54, C56: 10uF; C0805
C49, C52, C53, C55, C57: 0.1uF; C0603
C50: CC0603; C0603
C58: 10pF; C0603
C59: 50pF; C0603
U8: AD5791BRUZ; SOP65P640X120-20N
U9: AD8676ARZ; SOIC127P600X175-8N

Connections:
+VPWR: C48.2, C49.2, C54.2, C55.2, U8.5 (VDD), U9.8 (V+); also elsewhere on the board
-VPWR: C51.2, C52.2, C56.2, C57.2, U8.18 (VSS), U9.4 (V-); also elsewhere on the board
ANALOG_REF: C53.1, U9.3 (+IN_A); also elsewhere on the board
DACO_3: C59.2, U8.2 (VOUT); also elsewhere on the board
DPWR: C50.2, U8.6 (~RESET), U8.7 (~CLR), U8.9 (VCC), U8.10 (IOVCC); also elsewhere on the board
GND: C48.1, C49.1, C50.1, C51.1, C52.1, C53.2, C54.1, C55.1, C56.1, C57.1, C59.1, U8.15 (DGND), U8.19 (AGND), U9.5 (+IN_B); also elsewhere on the board
INV_3: C58.1, U8.1 (INV); also elsewhere on the board
LDAC: U8.8 (~LDAC); also elsewhere on the board
unnamed: U8.4 (VREFPF), U9.1 (OUT_A)
unnamed: U8.16 (VREFNF), U9.7 (OUT_B)
unnamed: U8.3 (VREFPS), U9.2 (-IN_A)
unnamed: U8.17 (VREFNS), U9.6 (-IN_B)
RFB_3: C58.2, U8.20 (RFB); also elsewhere on the board
SCLK_3: U8.13 (SCLK); also elsewhere on the board
SDIN_3: U8.12 (SDIN); also elsewhere on the board
SDO_3: U8.11 (SDO)
SYNC_3: U8.14 (~SYNC); also elsewhere on the board

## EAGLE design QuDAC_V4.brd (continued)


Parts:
C60, C63, C66, C68: 10uF; C0805
C61, C64, C65, C67, C69: 0.1uF; C0603
C62: CC0603; C0603
C70: 10pF; C0603
C71: 50pF; C0603
U10: AD5791BRUZ; SOP65P640X120-20N
U11: AD8676ARZ; SOIC127P600X175-8N

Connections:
+VPWR: C60.2, C61.2, C66.2, C67.2, U10.5 (VDD), U11.8 (V+); also elsewhere on the board
-VPWR: C63.2, C64.2, C68.2, C69.2, U10.18 (VSS), U11.4 (V-); also elsewhere on the board
ANALOG_REF: C65.1, U11.3 (+IN_A); also elsewhere on the board
DACO_4: C71.2, U10.2 (VOUT); also elsewhere on the board
DPWR: C62.2, U10.6 (~RESET), U10.7 (~CLR), U10.9 (VCC), U10.10 (IOVCC); also elsewhere on the board
GND: C60.1, C61.1, C62.1, C63.1, C64.1, C65.2, C66.1, C67.1, C68.1, C69.1, C71.1, U10.15 (DGND), U10.19 (AGND), U11.5 (+IN_B); also elsewhere on the board
INV_4: C70.1, U10.1 (INV); also elsewhere on the board
LDAC: U10.8 (~LDAC); also elsewhere on the board
unnamed: U10.4 (VREFPF), U11.1 (OUT_A)
unnamed: U10.16 (VREFNF), U11.7 (OUT_B)
unnamed: U10.3 (VREFPS), U11.2 (-IN_A)
unnamed: U10.17 (VREFNS), U11.6 (-IN_B)
RFB_4: C70.2, U10.20 (RFB); also elsewhere on the board
SCLK_4: U10.13 (SCLK); also elsewhere on the board
SDIN_4: U10.12 (SDIN); also elsewhere on the board
SDO_4: U10.11 (SDO)
SYNC_4: U10.14 (~SYNC); also elsewhere on the board


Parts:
C72, C75, C78, C80: 10uF; C0805
C73, C76, C77, C79, C81: 0.1uF; C0603
C74: CC0603; C0603
C82: 10pF; C0603
C83: 50pF; C0603
U12: AD5791BRUZ; SOP65P640X120-20N
U13: AD8676ARZ; SOIC127P600X175-8N

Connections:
+VPWR: C72.2, C73.2, C78.2, C79.2, U12.5 (VDD), U13.8 (V+); also elsewhere on the board
-VPWR: C75.2, C76.2, C80.2, C81.2, U12.18 (VSS), U13.4 (V-); also elsewhere on the board
ANALOG_REF: C77.1, U13.3 (+IN_A); also elsewhere on the board
DACO_5: C83.2, U12.2 (VOUT); also elsewhere on the board
DPWR: C74.2, U12.6 (~RESET), U12.7 (~CLR), U12.9 (VCC), U12.10 (IOVCC); also elsewhere on the board
GND: C72.1, C73.1, C74.1, C75.1, C76.1, C77.2, C78.1, C79.1, C80.1, C81.1, C83.1, U12.15 (DGND), U12.19 (AGND), U13.5 (+IN_B); also elsewhere on the board
INV_5: C82.1, U12.1 (INV); also elsewhere on the board
LDAC: U12.8 (~LDAC); also elsewhere on the board
unnamed: U12.4 (VREFPF), U13.1 (OUT_A)
unnamed: U12.16 (VREFNF), U13.7 (OUT_B)
unnamed: U12.3 (VREFPS), U13.2 (-IN_A)
unnamed: U12.17 (VREFNS), U13.6 (-IN_B)
RFB_5: C82.2, U12.20 (RFB); also elsewhere on the board
SCLK_5: U12.13 (SCLK); also elsewhere on the board
SDIN_5: U12.12 (SDIN); also elsewhere on the board
SDO_5: U12.11 (SDO)
SYNC_5: U12.14 (~SYNC); also elsewhere on the board


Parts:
C84, C87, C90, C92: 10uF; C0805
C85, C88, C89, C91, C93: 0.1uF; C0603
C86: CC0603; C0603
C94: 10pF; C0603
C95: 50pF; C0603
U14: AD5791BRUZ; SOP65P640X120-20N
U15: AD8676ARZ; SOIC127P600X175-8N

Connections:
+VPWR: C84.2, C85.2, C90.2, C91.2, U14.5 (VDD), U15.8 (V+); also elsewhere on the board
-VPWR: C87.2, C88.2, C92.2, C93.2, U14.18 (VSS), U15.4 (V-); also elsewhere on the board
ANALOG_REF: C89.1, U15.3 (+IN_A); also elsewhere on the board
DACO_6: C95.2, U14.2 (VOUT); also elsewhere on the board
DPWR: C86.2, U14.6 (~RESET), U14.7 (~CLR), U14.9 (VCC), U14.10 (IOVCC); also elsewhere on the board
GND: C84.1, C85.1, C86.1, C87.1, C88.1, C89.2, C90.1, C91.1, C92.1, C93.1, C95.1, U14.15 (DGND), U14.19 (AGND), U15.5 (+IN_B); also elsewhere on the board
INV_6: C94.1, U14.1 (INV); also elsewhere on the board
LDAC: U14.8 (~LDAC); also elsewhere on the board
unnamed: U14.4 (VREFPF), U15.1 (OUT_A)
unnamed: U14.16 (VREFNF), U15.7 (OUT_B)
unnamed: U14.3 (VREFPS), U15.2 (-IN_A)
unnamed: U14.17 (VREFNS), U15.6 (-IN_B)
RFB_6: C94.2, U14.20 (RFB); also elsewhere on the board
SCLK_6: U14.13 (SCLK); also elsewhere on the board
SDIN_6: U14.12 (SDIN); also elsewhere on the board
SDO_6: U14.11 (SDO)
SYNC_6: U14.14 (~SYNC); also elsewhere on the board

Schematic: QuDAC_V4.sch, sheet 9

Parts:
C96, C99, C102, C104: 10uF; C0805
C97, C100, C101, C103, C105: 0.1uF; C0603
C98: CC0603; C0603
C106: 10pF; C0603
C107: 50pF; C0603
U16: AD5791BRUZ; SOP65P640X120-20N
U17: AD8676ARZ; SOIC127P600X175-8N

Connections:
+VPWR: C96.2, C97.2, C102.2, C103.2, U16.5 (VDD), U17.8 (V+); also elsewhere on the board
-VPWR: C99.2, C100.2, C104.2, C105.2, U16.18 (VSS), U17.4 (V-); also elsewhere on the board
ANALOG_REF: C101.1, U17.3 (+IN_A); also elsewhere on the board
DACO_7: C107.2, U16.2 (VOUT); also elsewhere on the board
DPWR: C98.2, U16.6 (~RESET), U16.7 (~CLR), U16.9 (VCC), U16.10 (IOVCC); also elsewhere on the board
GND: C96.1, C97.1, C98.1, C99.1, C100.1, C101.2, C102.1, C103.1, C104.1, C105.1, C107.1, U16.15 (DGND), U16.19 (AGND), U17.5 (+IN_B); also elsewhere on the board
INV_7: C106.1, U16.1 (INV); also elsewhere on the board
LDAC: U16.8 (~LDAC); also elsewhere on the board
unnamed: U16.4 (VREFPF), U17.1 (OUT_A)
unnamed: U16.16 (VREFNF), U17.7 (OUT_B)
unnamed: U16.3 (VREFPS), U17.2 (-IN_A)
unnamed: U16.17 (VREFNS), U17.6 (-IN_B)
RFB_7: C106.2, U16.20 (RFB); also elsewhere on the board
SCLK_7: U16.13 (SCLK); also elsewhere on the board
SDIN_7: U16.12 (SDIN); also elsewhere on the board
SDO_7: U16.11 (SDO)
SYNC_7: U16.14 (~SYNC); also elsewhere on the board

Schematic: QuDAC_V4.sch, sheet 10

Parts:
C108, C111, C114, C116: 10uF; C0805
C109, C112, C113, C115, C117: 0.1uF; C0603
C110: CC0603; C0603
C118: 10pF; C0603
C119: 50pF; C0603
U18: AD5791BRUZ; SOP65P640X120-20N
U19: AD8676ARZ; SOIC127P600X175-8N

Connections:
+VPWR: C108.2, C109.2, C114.2, C115.2, U18.5 (VDD), U19.8 (V+); also elsewhere on the board
-VPWR: C111.2, C112.2, C116.2, C117.2, U18.18 (VSS), U19.4 (V-); also elsewhere on the board
ANALOG_REF: C113.1, U19.3 (+IN_A); also elsewhere on the board
DACO_8: C119.2, U18.2 (VOUT); also elsewhere on the board
DPWR: C110.2, U18.6 (~RESET), U18.7 (~CLR), U18.9 (VCC), U18.10 (IOVCC); also elsewhere on the board
GND: C108.1, C109.1, C110.1, C111.1, C112.1, C113.2, C114.1, C115.1, C116.1, C117.1, C119.1, U18.15 (DGND), U18.19 (AGND), U19.5 (+IN_B); also elsewhere on the board
INV_8: C118.1, U18.1 (INV); also elsewhere on the board
LDAC: U18.8 (~LDAC); also elsewhere on the board
unnamed: U18.4 (VREFPF), U19.1 (OUT_A)
unnamed: U18.16 (VREFNF), U19.7 (OUT_B)
unnamed: U18.3 (VREFPS), U19.2 (-IN_A)
unnamed: U18.17 (VREFNS), U19.6 (-IN_B)
RFB_8: C118.2, U18.20 (RFB); also elsewhere on the board
SCLK_8: U18.13 (SCLK); also elsewhere on the board
SDIN_8: U18.12 (SDIN); also elsewhere on the board
SDO_8: U18.11 (SDO)
SYNC_8: U18.14 (~SYNC); also elsewhere on the board

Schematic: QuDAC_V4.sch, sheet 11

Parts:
C120, C123, C126, C128: 10uF; C0805
C121, C124, C125, C127, C129: 0.1uF; C0603
C122: CC0603; C0603
C130: 10pF; C0603
C131: 50pF; C0603
U20: AD5791BRUZ; SOP65P640X120-20N
U21: AD8676ARZ; SOIC127P600X175-8N

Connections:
+VPWR: C120.2, C121.2, C126.2, C127.2, U20.5 (VDD), U21.8 (V+); also elsewhere on the board
-VPWR: C123.2, C124.2, C128.2, C129.2, U20.18 (VSS), U21.4 (V-); also elsewhere on the board
ANALOG_REF: C125.1, U21.3 (+IN_A); also elsewhere on the board
DACO_9: C131.2, U20.2 (VOUT); also elsewhere on the board
DPWR: C122.2, U20.6 (~RESET), U20.7 (~CLR), U20.9 (VCC), U20.10 (IOVCC); also elsewhere on the board
GND: C120.1, C121.1, C122.1, C123.1, C124.1, C125.2, C126.1, C127.1, C128.1, C129.1, C131.1, U20.15 (DGND), U20.19 (AGND), U21.5 (+IN_B); also elsewhere on the board
INV_9: C130.1, U20.1 (INV); also elsewhere on the board
LDAC: U20.8 (~LDAC); also elsewhere on the board
unnamed: U20.4 (VREFPF), U21.1 (OUT_A)
unnamed: U20.16 (VREFNF), U21.7 (OUT_B)
unnamed: U20.3 (VREFPS), U21.2 (-IN_A)
unnamed: U20.17 (VREFNS), U21.6 (-IN_B)
RFB_9: C130.2, U20.20 (RFB); also elsewhere on the board
SCLK_9: U20.13 (SCLK); also elsewhere on the board
SDIN_9: U20.12 (SDIN); also elsewhere on the board
SDO_9: U20.11 (SDO)
SYNC_9: U20.14 (~SYNC); also elsewhere on the board

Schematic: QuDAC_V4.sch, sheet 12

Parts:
C132, C135, C138, C140: 10uF; C0805
C133, C136, C137, C139, C141: 0.1uF; C0603
C134: CC0603; C0603
C142: 10pF; C0603
C143: 50pF; C0603
U22: AD5791BRUZ; SOP65P640X120-20N
U23: AD8676ARZ; SOIC127P600X175-8N

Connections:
+VPWR: C132.2, C133.2, C138.2, C139.2, U22.5 (VDD), U23.8 (V+); also elsewhere on the board
-VPWR: C135.2, C136.2, C140.2, C141.2, U22.18 (VSS), U23.4 (V-); also elsewhere on the board
ANALOG_REF: C137.1, U23.3 (+IN_A); also elsewhere on the board
DACO_10: C143.2, U22.2 (VOUT); also elsewhere on the board
DPWR: C134.2, U22.6 (~RESET), U22.7 (~CLR), U22.9 (VCC), U22.10 (IOVCC); also elsewhere on the board
GND: C132.1, C133.1, C134.1, C135.1, C136.1, C137.2, C138.1, C139.1, C140.1, C141.1, C143.1, U22.15 (DGND), U22.19 (AGND), U23.5 (+IN_B); also elsewhere on the board
INV_10: C142.1, U22.1 (INV); also elsewhere on the board
LDAC: U22.8 (~LDAC); also elsewhere on the board
unnamed: U22.4 (VREFPF), U23.1 (OUT_A)
unnamed: U22.16 (VREFNF), U23.7 (OUT_B)
unnamed: U22.3 (VREFPS), U23.2 (-IN_A)
unnamed: U22.17 (VREFNS), U23.6 (-IN_B)
RFB_10: C142.2, U22.20 (RFB); also elsewhere on the board
SCLK_10: U22.13 (SCLK); also elsewhere on the board
SDIN_10: U22.12 (SDIN); also elsewhere on the board
SDO_10: U22.11 (SDO)
SYNC_10: U22.14 (~SYNC); also elsewhere on the board

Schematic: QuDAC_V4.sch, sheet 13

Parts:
C144, C147, C150, C152: 10uF; C0805
C145, C148, C149, C151, C153: 0.1uF; C0603
C146: CC0603; C0603
C154: 10pF; C0603
C155: 50pF; C0603
U24: AD5791BRUZ; SOP65P640X120-20N
U25: AD8676ARZ; SOIC127P600X175-8N

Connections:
+VPWR: C144.2, C145.2, C150.2, C151.2, U24.5 (VDD), U25.8 (V+); also elsewhere on the board
-VPWR: C147.2, C148.2, C152.2, C153.2, U24.18 (VSS), U25.4 (V-); also elsewhere on the board
ANALOG_REF: C149.1, U25.3 (+IN_A); also elsewhere on the board
DACO_11: C155.2, U24.2 (VOUT); also elsewhere on the board
DPWR: C146.2, U24.6 (~RESET), U24.7 (~CLR), U24.9 (VCC), U24.10 (IOVCC); also elsewhere on the board
GND: C144.1, C145.1, C146.1, C147.1, C148.1, C149.2, C150.1, C151.1, C152.1, C153.1, C155.1, U24.15 (DGND), U24.19 (AGND), U25.5 (+IN_B); also elsewhere on the board
INV_11: C154.1, U24.1 (INV); also elsewhere on the board
LDAC: U24.8 (~LDAC); also elsewhere on the board
unnamed: U24.4 (VREFPF), U25.1 (OUT_A)
unnamed: U24.16 (VREFNF), U25.7 (OUT_B)
unnamed: U24.3 (VREFPS), U25.2 (-IN_A)
unnamed: U24.17 (VREFNS), U25.6 (-IN_B)
RFB_11: C154.2, U24.20 (RFB); also elsewhere on the board
SCLK_11: U24.13 (SCLK); also elsewhere on the board
SDIN_11: U24.12 (SDIN); also elsewhere on the board
SDO_11: U24.11 (SDO)
SYNC_11: U24.14 (~SYNC); also elsewhere on the board

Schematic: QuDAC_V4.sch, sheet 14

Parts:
C156, C159, C162, C164: 10uF; C0805
C157, C160, C161, C163, C165: 0.1uF; C0603
C158: CC0603; C0603
C166: 10pF; C0603
C167: 50pF; C0603
U26: AD5791BRUZ; SOP65P640X120-20N
U27: AD8676ARZ; SOIC127P600X175-8N

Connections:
+VPWR: C156.2, C157.2, C162.2, C163.2, U26.5 (VDD), U27.8 (V+); also elsewhere on the board
-VPWR: C159.2, C160.2, C164.2, C165.2, U26.18 (VSS), U27.4 (V-); also elsewhere on the board
ANALOG_REF: C161.1, U27.3 (+IN_A); also elsewhere on the board
DACO_12: C167.2, U26.2 (VOUT); also elsewhere on the board
DPWR: C158.2, U26.6 (~RESET), U26.7 (~CLR), U26.9 (VCC), U26.10 (IOVCC); also elsewhere on the board
GND: C156.1, C157.1, C158.1, C159.1, C160.1, C161.2, C162.1, C163.1, C164.1, C165.1, C167.1, U26.15 (DGND), U26.19 (AGND), U27.5 (+IN_B); also elsewhere on the board
INV_12: C166.1, U26.1 (INV); also elsewhere on the board
LDAC: U26.8 (~LDAC); also elsewhere on the board
unnamed: U26.4 (VREFPF), U27.1 (OUT_A)
unnamed: U26.16 (VREFNF), U27.7 (OUT_B)
unnamed: U26.3 (VREFPS), U27.2 (-IN_A)
unnamed: U26.17 (VREFNS), U27.6 (-IN_B)
RFB_12: C166.2, U26.20 (RFB); also elsewhere on the board
SCLK_12: U26.13 (SCLK); also elsewhere on the board
SDIN_12: U26.12 (SDIN); also elsewhere on the board
SDO_12: U26.11 (SDO)
SYNC_12: U26.14 (~SYNC); also elsewhere on the board



Board: 6 copper layers, 166.0 x 100.5 mm, 270 parts (128 on the bottom side), 263 nets.

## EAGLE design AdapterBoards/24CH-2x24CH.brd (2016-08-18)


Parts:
IN: F50VP
OUT1, OUT2, OUT3: M50VP

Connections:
GND1: IN.G1, IN.G2, OUT1.G1, OUT1.G2, OUT2.G1, OUT2.G2, OUT3.G1, OUT3.G2
unnamed: IN.35, OUT1.35, OUT2.35, OUT3.35
unnamed: IN.38, OUT1.38, OUT2.38, OUT3.38
unnamed: IN.1, OUT1.1, OUT2.1, OUT3.1
unnamed: IN.18, OUT1.18, OUT2.18, OUT3.18
unnamed: IN.2, OUT1.2, OUT2.2, OUT3.2
unnamed: IN.19, OUT1.19, OUT2.19, OUT3.19
unnamed: IN.3, OUT1.3, OUT2.3, OUT3.3
unnamed: IN.20, OUT1.20, OUT2.20, OUT3.20
unnamed: IN.4, OUT1.4, OUT2.4, OUT3.4
unnamed: IN.21, OUT1.21, OUT2.21, OUT3.21
unnamed: IN.5, OUT1.5, OUT2.5, OUT3.5
unnamed: IN.22, OUT1.22, OUT2.22, OUT3.22
unnamed: IN.6, OUT1.6, OUT2.6, OUT3.6
unnamed: IN.23, OUT1.23, OUT2.23, OUT3.23
unnamed: IN.7, OUT1.7, OUT2.7, OUT3.7
unnamed: IN.24, OUT1.24, OUT2.24, OUT3.24
unnamed: IN.8, OUT1.8, OUT2.8, OUT3.8
unnamed: IN.25, OUT1.25, OUT2.25, OUT3.25
unnamed: IN.9, OUT1.9, OUT2.9, OUT3.9
unnamed: IN.26, OUT1.26, OUT2.26, OUT3.26
unnamed: IN.10, OUT1.10, OUT2.10, OUT3.10
unnamed: IN.27, OUT1.27, OUT2.27, OUT3.27
unnamed: IN.11, OUT1.11, OUT2.11, OUT3.11
unnamed: IN.28, OUT1.28, OUT2.28, OUT3.28
unnamed: IN.12, OUT1.12, OUT2.12, OUT3.12
unnamed: IN.29, OUT1.29, OUT2.29, OUT3.29
unnamed: IN.13, OUT1.13, OUT2.13, OUT3.13
unnamed: IN.30, OUT1.30, OUT2.30, OUT3.30
unnamed: IN.14, OUT1.14, OUT2.14, OUT3.14
unnamed: IN.31, OUT1.31, OUT2.31, OUT3.31
unnamed: IN.15, OUT1.15, OUT2.15, OUT3.15
unnamed: IN.32, OUT1.32, OUT2.32, OUT3.32
unnamed: IN.16, OUT1.16, OUT2.16, OUT3.16
unnamed: IN.33, OUT1.33, OUT2.33, OUT3.33
unnamed: IN.17, OUT1.17, OUT2.17, OUT3.17
unnamed: IN.40, OUT1.40, OUT2.40, OUT3.40
unnamed: IN.39, OUT1.39, OUT2.39, OUT3.39
unnamed: IN.34, OUT1.34, OUT2.34, OUT3.34
unnamed: IN.36, OUT1.36, OUT2.36, OUT3.36
unnamed: IN.37, OUT1.37, OUT2.37, OUT3.37
unnamed: IN.41, OUT1.41, OUT2.41, OUT3.41
unnamed: IN.42, OUT1.42, OUT2.42, OUT3.42
unnamed: IN.43, OUT1.43, OUT2.43, OUT3.43
unnamed: IN.44, OUT1.44, OUT2.44, OUT3.44
unnamed: IN.45, OUT1.45, OUT2.45, OUT3.45
unnamed: IN.46, OUT1.46, OUT2.46, OUT3.46
unnamed: IN.47, OUT1.47, OUT2.47, OUT3.47
unnamed: IN.48, OUT1.48, OUT2.48, OUT3.48
unnamed: IN.49, OUT1.49, OUT2.49, OUT3.49
unnamed: IN.50, OUT1.50, OUT2.50, OUT3.50



Board: 4 copper layers, 96.5 x 73.7 mm, 4 parts (2 on the bottom side), 51 nets.

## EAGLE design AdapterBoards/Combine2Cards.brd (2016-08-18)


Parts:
R2, R3, R4, R5: 0Ω; R0603
X1, X2: M50VP
X3: F50VP

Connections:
+12V: R2.1, X1.1, X1.2
-12V: R4.2, X2.34, X2.35
DCLK1_0: X1.50
DCLK1_1: X1.33
DCLK1_2: X1.16
DCLK1_3: X1.49
DCLK1_5: X1.17
DCLK2_0: X2.50
DCLK2_1: X2.33
DCLK2_2: X2.16
DCLK2_3: X2.49
DCLK2_5: X2.17
GND: R3.2, R5.2, X1.3, X1.5, X1.7, X1.9, X1.11, X1.13, X1.15, X1.18, X1.19, X1.20, X1.21, X1.22, X1.23, X1.24, X1.25, X1.26, X1.27, X1.28, X1.29, X1.30, X1.31, X1.32, X1.36, X1.38, X1.40, X1.42, X1.44, X1.46, X1.48, X2.3, X2.5, X2.7, X2.9, X2.11, X2.13, X2.15, X2.18, X2.19, X2.20, X2.21, X2.22, X2.23, X2.24, X2.25, X2.26, X2.27, X2.28, X2.29, X2.30, X2.31, X2.32, X2.36, X2.38, X2.40, X2.42, X2.44, X2.46, X2.48, X3.1, X3.3, X3.5, X3.7, X3.9, X3.11, X3.13, X3.19, X3.21, X3.23, X3.25, X3.27, X3.29, X3.34, X3.36, X3.38, X3.40, X3.42, X3.44, X3.46
unnamed: R2.2, R3.1, X3.17, X3.33, X3.50
unnamed: R4.1, R5.1, X3.15, X3.31, X3.48
SHIELDGND: X1.G1, X1.G2, X2.G1, X2.G2, X3.G1, X3.G2
VOUT1_1: X1.8, X3.10
VOUT1_2: X1.41, X3.26
VOUT1_3: X1.6, X3.12
VOUT1_4: X1.39, X3.14
VOUT1_5: X1.37, X3.16
VOUT1_6: X1.4, X3.32
VOUT1_7: X1.14, X3.2
VOUT1_8: X1.47, X3.18
VOUT1_9: X1.45, X3.20
VOUT1_10: X1.12, X3.4
VOUT1_11: X1.43, X3.6
VOUT1_12: X1.10, X3.8
VOUT2_1: X2.8, X3.43
VOUT2_2: X2.41, X3.28
VOUT2_3: X2.6, X3.30
VOUT2_4: X2.39, X3.45
VOUT2_5: X2.37, X3.47
VOUT2_6: X2.4, X3.49
VOUT2_7: X2.14, X3.35
VOUT2_8: X2.47, X3.37
VOUT2_9: X2.45, X3.39
VOUT2_10: X2.12, X3.22
VOUT2_11: X2.43, X3.41
VOUT2_12: X2.10, X3.24



Board: 2 copper layers, 51.0 x 68.0 mm, 7 parts (2 on the bottom side), 30 nets.

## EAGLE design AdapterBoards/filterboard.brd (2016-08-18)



Board: 4 copper layers, 111.8 x 102.9 mm, 64 parts (31 on the bottom side), 101 nets.

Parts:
C1: 1pF; C0805
C2: 1000pF; C0805
CM1, CM2, CM3, CM4, CM5, CM6: C5B4.5
R1, R2: R0603
U$1, U$2, U$3, U$4, U$5, U$6, U$7, U$8, U$9, U$10, U$11, U$12, U$13, U$14, U$15, U$16, U$17, U$18, U$19, U$20, U$21, U$22, U$23, U$24, U$25, U$26, U$27, U$28, U$29, U$30, U$31, U$32, U$33, U$34, U$35, U$36, U$37, U$38, U$39, U$40, U$41, U$42, U$43, U$44, U$45, U$46, U$47, U$48: COILCRAFT-LC7POLE
U$49: XINDUCTOR
X1, X2, X3: F50HP
X4: RF IN; J502-ND-142-0711-821/826
X5: RF tap; J502-ND-142-0711-821/826

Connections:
GND: C2.2, CM1.1, CM2.1, CM3.1, CM4.1, CM5.1, CM6.1, R2.1, U$1.GND0, U$1.GND1, U$1.GND2, U$1.GND3, U$1.NC0, U$1.NC1, U$2.GND0, U$2.GND1, U$2.GND2, U$2.GND3, U$2.NC0, U$2.NC1, U$3.GND0, U$3.GND1, U$3.GND2, U$3.GND3, U$3.NC0, U$3.NC1, U$4.GND0, U$4.GND1, U$4.GND2, U$4.GND3, U$4.NC0, U$4.NC1, U$5.GND0, U$5.GND1, U$5.GND2, U$5.GND3, U$5.NC0, U$5.NC1, U$6.GND0, U$6.GND1, U$6.GND2, U$6.GND3, U$6.NC0, U$6.NC1, U$7.GND0, U$7.GND1, U$7.GND2, U$7.GND3, U$7.NC0, U$7.NC1, U$8.GND0, U$8.GND1, U$8.GND2, U$8.GND3, U$8.NC0, U$8.NC1, U$9.GND0, U$9.GND1, U$9.GND2, U$9.GND3, U$9.NC0, U$9.NC1, U$10.GND0, U$10.GND1, U$10.GND2, U$10.GND3, U$10.NC0, U$10.NC1, U$11.GND0, U$11.GND1, U$11.GND2, U$11.GND3, U$11.NC0, U$11.NC1, U$12.GND0, U$12.GND1, U$12.GND2, U$12.GND3, U$12.NC0, U$12.NC1, U$13.GND0, U$13.GND1, U$13.GND2, U$13.GND3, U$13.NC0, U$13.NC1, U$14.GND0, U$14.GND1, U$14.GND2, U$14.GND3, U$14.NC0, U$14.NC1, U$15.GND0, U$15.GND1, U$15.GND2, U$15.GND3, U$15.NC0, U$15.NC1, U$16.GND0, U$16.GND1, U$16.GND2, U$16.GND3, U$16.NC0, U$16.NC1, U$17.GND0, U$17.GND1, U$17.GND2, U$17.GND3, U$17.NC0, U$17.NC1, U$18.GND0, U$18.GND1, U$18.GND2, U$18.GND3, U$18.NC0, U$18.NC1, U$19.GND0, U$19.GND1, U$19.GND2, U$19.GND3, U$19.NC0, U$19.NC1, U$20.GND0, U$20.GND1, U$20.GND2, U$20.GND3, U$20.NC0, U$20.NC1, U$21.GND0, U$21.GND1, U$21.GND2, U$21.GND3, U$21.NC0, U$21.NC1, U$22.GND0, U$22.GND1, U$22.GND2, U$22.GND3, U$22.NC0, U$22.NC1, U$23.GND0, U$23.GND1, U$23.GND2, U$23.GND3, U$23.NC0, U$23.NC1, U$24.GND0, U$24.GND1, U$24.GND2, U$24.GND3, U$24.NC0, U$24.NC1, U$25.GND0, U$25.GND1, U$25.GND2, U$25.GND3, U$25.NC0, U$25.NC1, U$26.GND0, U$26.GND1, U$26.GND2, U$26.GND3, U$26.NC0, U$26.NC1, U$27.GND0, U$27.GND1, U$27.GND2, U$27.GND3, U$27.NC0, U$27.NC1, U$28.GND0, U$28.GND1, U$28.GND2, U$28.GND3, U$28.NC0, U$28.NC1, U$29.GND0, U$29.GND1, U$29.GND2, U$29.GND3, U$29.NC0, U$29.NC1, U$30.GND0, U$30.GND1, U$30.GND2, U$30.GND3, U$30.NC0, U$30.NC1, U$31.GND0, U$31.GND1, U$31.GND2, U$31.GND3, U$31.NC0, U$31.NC1, U$32.GND0, U$32.GND1, U$32.GND2, U$32.GND3, U$32.NC0, U$32.NC1, U$33.GND0, U$33.GND1, U$33.GND2, U$33.GND3, U$33.NC0, U$33.NC1, U$34.GND0, U$34.GND1, U$34.GND2, U$34.GND3, U$34.NC0, U$34.NC1, U$35.GND0, U$35.GND1, U$35.GND2, U$35.GND3, U$35.NC0, U$35.NC1, U$36.GND0, U$36.GND1, U$36.GND2, U$36.GND3, U$36.NC0, U$36.NC1, U$37.GND0, U$37.GND1, U$37.GND2, U$37.GND3, U$37.NC0, U$37.NC1, U$38.GND0, U$38.GND1, U$38.GND2, U$38.GND3, U$38.NC0, U$38.NC1, U$39.GND0, U$39.GND1, U$39.GND2, U$39.GND3, U$39.NC0, U$39.NC1, U$40.GND0, U$40.GND1, U$40.GND2, U$40.GND3, U$40.NC0, U$40.NC1, U$41.GND0, U$41.GND1, U$41.GND2, U$41.GND3, U$41.NC0, U$41.NC1, U$42.GND0, U$42.GND1, U$42.GND2, U$42.GND3, U$42.NC0, U$42.NC1, U$43.GND0, U$43.GND1, U$43.GND2, U$43.GND3, U$43.NC0, U$43.NC1, U$44.GND0, U$44.GND1, U$44.GND2, U$44.GND3, U$44.NC0, U$44.NC1, U$45.GND0, U$45.GND1, U$45.GND2, U$45.GND3, U$45.NC0, U$45.NC1, U$46.GND0, U$46.GND1, U$46.GND2, U$46.GND3, U$46.NC0, U$46.NC1, U$47.GND0, U$47.GND1, U$47.GND2, U$47.GND3, U$47.NC0, U$47.NC1, U$48.GND0, U$48.GND1, U$48.GND2, U$48.GND3, U$48.NC0, U$48.NC1, X1.G1, X1.G2, X2.1, X2.3, X2.5, X2.7, X2.9, X2.11, X2.13, X2.15, X2.17, X2.19, X2.21, X2.23, X2.25, X2.27, X2.29, X2.31, X2.33, X2.34, X2.36, X2.38, X2.40, X2.42, X2.44, X2.46, X2.48, X2.50, X3.1, X3.3, X3.5, X3.7, X3.9, X3.11, X3.13, X3.15, X3.17, X3.19, X3.21, X3.23, X3.25, X3.27, X3.29, X3.31, X3.33, X3.34, X3.36, X3.38, X3.40, X3.42, X3.44, X3.46, X3.48, X3.50, X4.G@1, X4.G@2, X5.G@1, X5.G@2
unnamed: C1.2, C2.1, X5.1
unnamed: R1.2, X1.25
S$1: U$49.INPUT3, U$49.OUTPUT1, U$49.OUTPUT2, X1.9
S$2: CM1.2, CM2.2, CM3.2, CM4.2, CM5.2, CM6.2, U$49.INPUT, U$49.INPUT2, X4.1
S$3: U$7.FILTER-OUTPUT, X1.34
S$4: U$9.FILTER-OUTPUT, X1.35
S$5: U$8.FILTER-OUTPUT, X1.36
S$6: U$22.FILTER-OUTPUT, X1.37
S$7: U$21.FILTER-OUTPUT, X1.38
S$8: U$42.FILTER-OUTPUT, X1.39
S$9: U$5.FILTER-OUTPUT, X1.40
S$10: U$12.FILTER-OUTPUT, X1.18
S$11: U$43.FILTER-OUTPUT, X1.19
S$12: U$36.FILTER-OUTPUT, X1.20
S$13: U$2.FILTER-OUTPUT, X1.21
S$14: U$3.FILTER-OUTPUT, X1.22
S$15: U$4.FILTER-OUTPUT, X1.23
S$16: U$6.FILTER-OUTPUT, X1.24
S$17: U$47.FILTER-OUTPUT, X1.41
S$18: U$46.FILTER-OUTPUT, X1.42
S$19: U$35.FILTER-OUTPUT, X1.1
S$20: U$18.FILTER-OUTPUT, X1.2
S$21: U$19.FILTER-OUTPUT, X1.3
S$22: U$20.FILTER-OUTPUT, X1.4
S$23: U$41.FILTER-OUTPUT, X1.5
S$24: U$11.FILTER-OUTPUT, X1.6
S$25: U$34.FILTER-OUTPUT, X1.7
S$26: U$10.FILTER-OUTPUT, X1.8
S$27: U$35.FILTER-INPUT, U$35.NC2, X2.18
S$28: U$18.FILTER-INPUT, U$18.NC2, X2.35
S$29: U$19.FILTER-INPUT, U$19.NC2, X2.2
S$30: U$20.NC2, X2.20
S$31: U$41.FILTER-INPUT, U$41.NC2, X2.37
S$32: U$11.FILTER-INPUT, U$11.NC2, X2.4
S$33: U$34.FILTER-INPUT, U$34.NC2, X2.22
S$34: U$10.FILTER-INPUT, U$10.NC2, X2.39
S$35: U$12.FILTER-INPUT, U$12.NC2, X2.6
S$36: U$43.FILTER-INPUT, U$43.NC2, X2.24
S$37: U$36.FILTER-INPUT, U$36.NC2, X2.41
S$38: U$2.FILTER-INPUT, U$2.NC2, X2.8
S$39: U$3.FILTER-INPUT, U$3.NC2, X2.26
S$40: U$4.FILTER-INPUT, U$4.NC2, X2.43
S$41: U$6.FILTER-INPUT, U$6.NC2, X2.10
S$42: U$46.FILTER-INPUT, U$46.NC2, X2.28
S$43: U$47.FILTER-INPUT, U$47.NC2, X2.12
S$44: U$5.FILTER-INPUT, U$5.NC2, X2.45
S$45: U$42.FILTER-INPUT, U$42.NC2, X2.30
S$46: U$21.FILTER-INPUT, U$21.NC2, X2.14
S$47: U$22.FILTER-INPUT, U$22.NC2, X2.47
S$48: U$8.FILTER-INPUT, U$8.NC2, X2.32
S$49: U$9.FILTER-INPUT, U$9.NC2, X2.16
S$50: U$7.FILTER-INPUT, U$7.NC2, X2.49
S$51: U$17.FILTER-OUTPUT, X1.50
S$52: U$24.FILTER-OUTPUT, X1.49
S$53: U$23.FILTER-OUTPUT, X1.48
S$54: U$32.FILTER-OUTPUT, X1.47
S$55: U$31.FILTER-OUTPUT, X1.46
S$56: U$40.FILTER-OUTPUT, X1.45
S$57: U$15.FILTER-OUTPUT, X1.44
S$58: U$27.FILTER-OUTPUT, X1.33
S$59: U$44.FILTER-OUTPUT, X1.32
S$60: U$38.FILTER-OUTPUT, X1.31
S$61: U$1.FILTER-OUTPUT, X1.30
S$62: U$13.FILTER-OUTPUT, X1.29
S$63: U$14.FILTER-OUTPUT, X1.28
S$64: U$16.FILTER-OUTPUT, X1.27
S$65: U$48.FILTER-OUTPUT, X1.43
S$66: U$45.FILTER-OUTPUT, X1.26
S$67: U$37.FILTER-OUTPUT, X1.17
S$68: U$28.FILTER-OUTPUT, X1.16
S$69: U$29.FILTER-OUTPUT, X1.15
S$70: U$30.FILTER-OUTPUT, X1.14
S$71: U$39.FILTER-OUTPUT, X1.13
S$72: U$26.FILTER-OUTPUT, X1.12
S$73: U$33.FILTER-OUTPUT, X1.11
S$74: U$25.FILTER-OUTPUT, X1.10
S$75: U$37.FILTER-INPUT, U$37.NC2, X3.18
S$76: U$28.FILTER-INPUT, U$28.NC2, X3.35
S$77: U$29.FILTER-INPUT, U$29.NC2, X3.2
S$78: U$30.NC2, X3.20
S$79: U$39.FILTER-INPUT, U$39.NC2, X3.37
S$80: U$26.FILTER-INPUT, U$26.NC2, X3.4
S$81: U$33.FILTER-INPUT, U$33.NC2, X3.22
S$82: U$25.FILTER-INPUT, U$25.NC2, X3.39
S$83: U$27.FILTER-INPUT, U$27.NC2, X3.6
S$84: U$44.FILTER-INPUT, U$44.NC2, X3.24
S$85: U$38.FILTER-INPUT, U$38.NC2, X3.41
S$86: U$1.FILTER-INPUT, U$1.NC2, X3.8
S$87: U$13.FILTER-INPUT, U$13.NC2, X3.26
S$88: U$14.FILTER-INPUT, U$14.NC2, X3.43
S$89: U$16.FILTER-INPUT, U$16.NC2, X3.10
S$90: U$45.FILTER-INPUT, U$45.NC2, X3.28
S$91: U$48.FILTER-INPUT, U$48.NC2, X3.12
S$92: U$15.FILTER-INPUT, U$15.NC2, X3.45
S$93: U$40.FILTER-INPUT, U$40.NC2, X3.30
S$94: U$31.FILTER-INPUT, U$31.NC2, X3.14
S$95: U$32.FILTER-INPUT, U$32.NC2, X3.47
S$96: U$23.FILTER-INPUT, U$23.NC2, X3.32
S$97: U$24.FILTER-INPUT, U$24.NC2, X3.16
S$98: U$17.FILTER-INPUT, U$17.NC2, X3.49

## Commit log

2016-08-18 Added eagle files for QuDAC and supporting boards
    [Reference_Adapter_pastemask.dxf, filterboard.GBL, filterboard.GBO, filterboard.GBP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]
2016-08-18 Updated ignore ignore files.
    [24CH-2x24CH.brd, 24CH-2x24CH.sch, AD5791.brd, AD5791.sch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]
2016-08-18 organized, updated README
    [Reference_Adapter.brd, Reference_Adapter.sch]
2016-08-18 Updated readme, reorganized some files
    [AD5791.brd, AD5791.sch, AD5791_V2.brd, AD5791_V2.sch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]
